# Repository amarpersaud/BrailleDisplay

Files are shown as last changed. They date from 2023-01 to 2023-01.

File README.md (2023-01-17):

# Electronic Braille Display Module
Electronic Refreshable Braille Display Module (8 dot) which uses latching solenoids with an integrated microcontroller and H-bridge drivers to drive each dot.

The design is inspired by MOLBED, a design which uses a latching solenoid formed by a solenoid coil, two metric nuts or washers, and neodymium magnets alongside 3d printed components. Some aspects of this design are similar, including the solenoid style of actuation. Several iterations of the design exist.  

## Physical Design Versions

### Version A (discontinued)
The first design consideration (Version A) (discontinued) consisted of an solenoid powered device with a physical latching mechanism, rather than the magnetic mechanism of MOLBED. Due to its low actuation force, complexity, and issues with actuation errors due to physical loading while actuating, it is no longer a consideration. Another major downside to this design is that all solenoids representing an extended dot must be simultaneously powered due to the physical latching mechanism locking all 8 dots at the same time, increasing the instantaneous power draw. Version B and C are two separate branching models under consideration.

### Version B
Version B uses a directly actuated latching solenoid which utilizes the force of a magnet hold the solenoid in the top position, more similar to MOLBED. The design is altered to reduce part count and complexity while improving actuation and holding force, and giving space to integrate electronics. This produces a module which has self contained drivers, with high holding force in the extended position, and high actuation force.

### Version C
Version C uses a similar solenoid as is used in Version B, however its mechanism is similar to that of multi-layer devices. The patent on such devices is no longer active and thus such devices can be produced. This uses a moving ramped section to push the dots up and down. The ramp allows a greater mechanical advantage, raising the actuation force. The holding force is also extremely high, as the pin is physically blocked from moving downwards. 

Due to the physical advantage in actuation for Version C, a lower force is needed to actuate the dots, meaning a larger or less efficient solenoid can be used. This means that the rare earth magnets (e.g. neodymium magnets) used in Version B could be swapped for weaker but more renewable and cheaper magnets.

The disadvantage of the Version C design is that it is much less compact. This is potentially an acceptable tradeoff, as it could be cheaper and more environmentally friendly, while allowing more room for electronics, but is harder to tile in a multi-row display. Due to the tradeoffs, it was deemed better to explore and refine both options in order to determine which design holds the advantage.

## Electronics
Electronics design for the device involved creation of a development board, codevelopment of the firmware and hardware using the development board, and a final board design created based on the physical CAD design. 

The development board design is available in the Hardware folder, and involves a microcontroller which drives two shift registers to control four dual H-bridge drivers, thus one H-bridge per dot or solenoid. The board is fairly large with hand solderable 0603 components, with additional GPIO and headers for development of the TWI/I2C, USART, and SPI communication protocols.

The development of the final board is still in progress and will likely consist of several boards connected together in order to keep it compact enough to fit inside the module (limited in size by the Braille standard) while still using off the shelf components.

## Firmware
The firmware for the device is still being developed. The firmware running on the embedded microcontroller creates several virtual registers which can be written to or read. Particularly, the device maintains a single byte register representing the 8 dots to be displayed, feedback sensing of the dot positions, operation completion, error detection using position detection as closed loop feedback, and configuration such as wether to immediately display the dots when the register is written or to automatically attempt to re-write to the display should an error in a dot be detected.

The device ID consists of two bytes written to EEPROM, allowing overwriting of the ID should the firmware be flashed to use many characters on a single bus such as with TWI or USART without an explicit select pin as afforded by SPI. This also allows setting the hardware address during runtime, without reflashing the firmware.

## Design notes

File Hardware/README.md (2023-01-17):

# Hardware
The hardware consists of a 3d CAD model for the module, an external development board for driving the latching solenoids, and several PCBs that form the final driver for the embedded device. 

## Definitions
- Holding force - Force the extended dots can withstand before device failure or depression of dot
- Actuation force - Force that an individual dot is capable of exerting while extending

## CAD model
Inspiration for the design came from the MOLBED project, and some aspects of the design are similar, including the solenoid style of actuation. Several iterations of the design exist. The first design consideration (Version A) (discontinued) consisted of an solenoid powered device with a physical latching mechanism, rather than the magnetic mechanism of MOLBED. Due to its low actuation force, complexity, and issues with actuation errors due to physical loading while actuating, it is no longer a consideration. Version B and C are two separate branching models under consideration. 

Version B uses a directly actuated latching solenoid which utilizes the force of a magnet hold the solenoid in the top position, more similar to MOLBED. The design is altered to reduce part count and complexity while improving actuation and holding force, and giving space to integrate electronics. This produces a module which has self contained drivers, with high holding force in the extended position, and high actuation force.

Version C uses a similar solenoid as is used in Version B, however its mechanism is similar to that of multi-layer devices. The patent on such devices is no longer active and thus such devices can be produced. This uses a moving ramped section to push the dots up and down. The ramp allows a greater mechanical advantage, raising the actuation force. The holding force is also extremely high, as the pin is physically blocked from moving downwards. 

Due to the physical advantage in actuation, a lower force is needed to actuate the dots, meaning a larger or less efficient solenoid can be used. This means that the rare earth magnets (e.g. neodymium magnets) used in Version B could be swapped for weaker but more renewable and cheaper magnets.

The disadvantage of the Version C design is that it is much less compact. This is potentially an acceptable tradeoff, as it could be cheaper and more environmentally friendly, while allowing more room for electronics, but is harder to tile in a multi-row display. Due to the tradeoffs, it was deemed better to explore and refine both options in order to determine which design holds the advantage.

## Development board - V0.1

The development board is available in the Development board folder.

<p align="center">
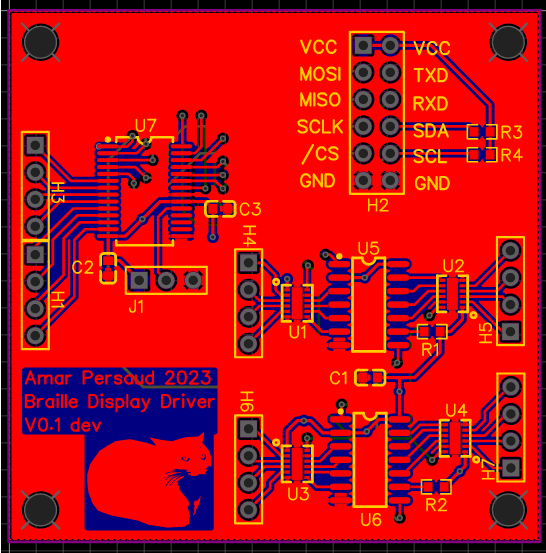
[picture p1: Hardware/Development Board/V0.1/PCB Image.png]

</p>

The board features an ATMEGA808-XUR microcontroller and two SN74HCS264DR shift registers to control four DRV8836DSSR ICs, each of which is capable of driving two bi-directional loads (headers H4-H7). Additionally, the header on the left (H1/H3) allows for 8x GPIO (for reading dot position for closed loop control), and the header on the top (H2) allows access to VCC(3.3V/5V), I2C/TWI, USART, and SPI communications. This allows for development of the software to communicate over SPI/USART/TWI with a higher level controller. Header J1 allows programming of the microcontroller via UPDI.

The board was developed in EasyEDA as it is a simple board whose sole purpose is to develop the firmware for the device; the board simply connects a microcontroller to shift registers, and shift registers to H-bridge drivers.

## Embedded PCB
The embedded device controller is currently in development. The device will be completed after finalization of the physical model.

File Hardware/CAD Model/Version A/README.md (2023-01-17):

# Version A
Version A consisted of an solenoid powered device with a physical latching mechanism, rather than the magnetic mechanism of MOLBED. 
Due to its low actuation force, complexity, and issues with actuation errors due to physical loading while actuating, it is no longer a consideration. 
Version A.1 and A.2 are two designs that are similar with slightly different operation. A.1 was the main design considered.

# Version A.1
Version A.1 is shown below: 
<p align="center">
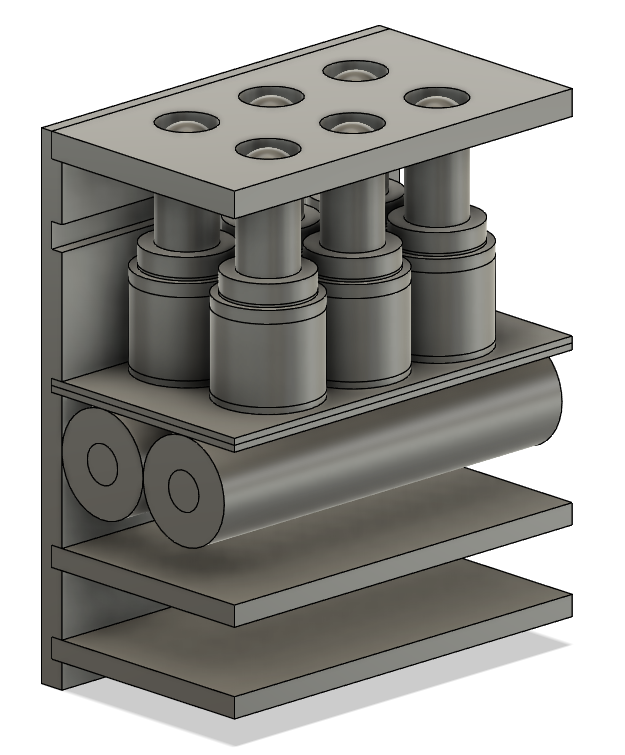
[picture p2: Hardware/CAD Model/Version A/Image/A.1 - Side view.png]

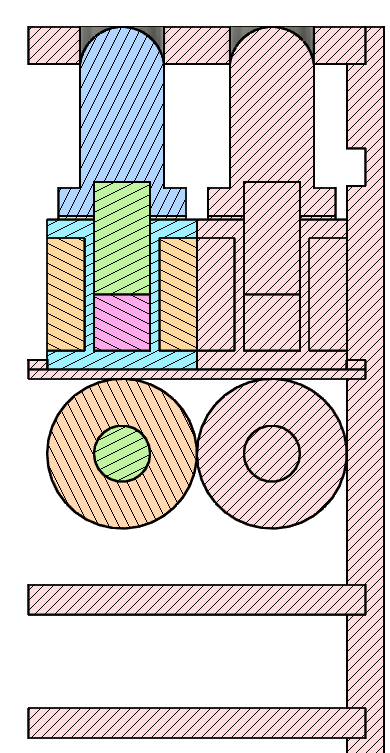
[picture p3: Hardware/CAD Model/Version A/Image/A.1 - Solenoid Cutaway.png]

</p>

The left wall is excluded for a better view of the internals, however it is identical to the right wall.

In the cutaway, the sections are labelled as follows:
- Blue - Plastic dot cap which the user physically interracts with
- Green - Iron or steel ferromagnetic rods
- Pink - Neodymium magnet
- Aqua - Plastic spool for holding the magnet wire which forms the solenoid
- Orange - Solenoid or electromagnet coil

The slot on the right wall allows for a sliding grid to be employed. When a dot is depressed, the bars of the grid go over the lip on the dot's cap. When a dot is extended, the bar passes below the lip and holds the dot up. This forms a physical latching mechanism. On the bottom, the horizontal electromagnet allows actuation of the grid via a lever linkage. Below the two electromagnets are two PCB layers with clearance for components. A ferromagnetic rod is used in the electromagnet to increase its strength, and in the solenoid to increase the permeability.

Issues with this design include low area on the circuit boards, a large space taken up by the electromagnets, high part count and complexity, susceptibility to wear and damage, a requirement for close tolerances, and the possibility for actuation failure.

# Version A.2
Version A.2 is shown below: 
<p align="center">
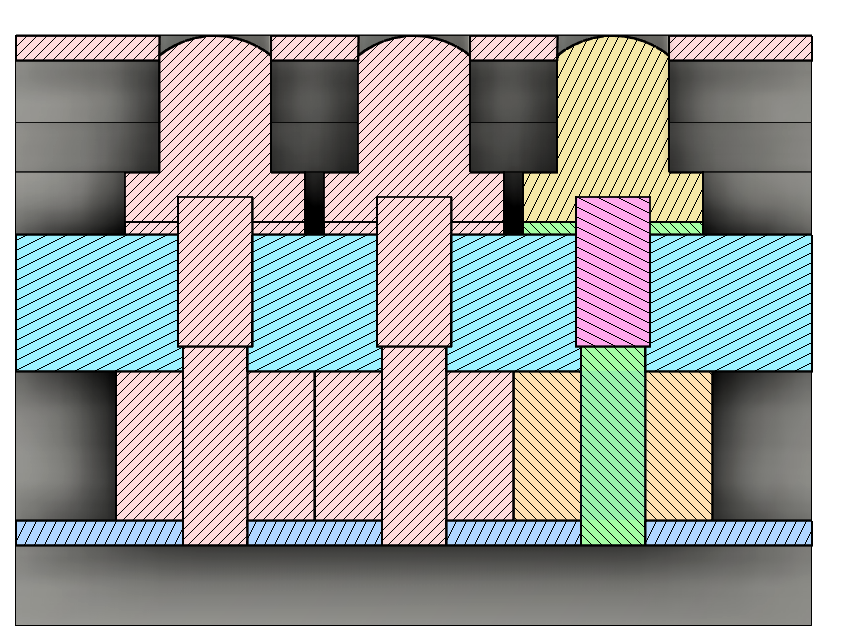
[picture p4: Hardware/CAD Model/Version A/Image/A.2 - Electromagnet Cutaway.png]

</p>

Version A.2 is design which takes a slightly different approach and was abandoned as well.

In the cutaway, the sections are labelled as follows:
- Yellow - Plastic dot cap which the user physically interracts with
- Horizontal Green Washer - Felt or soft material lower actuation noise
- Vertical Green Rod - Iron or steel ferromagnetic rods
- Pink - Neodymium magnet
- Aqua - Plastic for casing
- Blue - Plastic or PCB 
- Orange - Solenoid or electromagnet coil

This design has many drawbacks, including having a high retraction force but a much smaller actuation force, and relying on the physical actuation gives higher complexity.

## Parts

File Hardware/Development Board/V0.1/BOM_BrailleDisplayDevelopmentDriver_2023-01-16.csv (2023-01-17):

ID | Name | Designator | Footprint | Quantity | Manufacturer Part | Manufacturer | Supplier | Supplier Part | Price
1 | 0.1u | C1,C2,C3 | C0603 | 3
2 | HDR-F-2.54_1x4 | H1,H3,H4,H5,H6,H7 | HDR-F-2.54_1X4 | 6 |  |  | LCSC | C225501 | 0.013
3 | HDR-F-2.54_2x6 | H2 | HDR-F-2.54_2X6 | 1 |  |  | LCSC | C36191 | 0.011
4 | HDR-M-2.54_1x3 | J1 | HDR-M-2.54_1X3 | 1 |  |  | LCSC | C180248 | 0.031
5 | 1k | R1,R2 | R0603 | 2
6 | 4.7k | R3,R4 | R0603 | 2
7 | DRV8836DSSR | U1,U2,U3,U4 | WSON-12_L2.0-W3.0-P0.50-BL-EP | 4 | DRV8836DSSR | TI(德州仪器) | LCSC | C191002 | 0.249
8 | SN74HCS264DR | U5,U6 | SOIC-14_L8.6-W3.9-P1.27-LS6.0-BL | 2 | SN74HCS264DR | TI(德州仪器) | LCSC | C2861157 | 0.019
9 | ATMEGA808-XUR | U7 | SSOP-28_L10.2-W5.3-P0.65-LS7.8-BL | 1 | ATMEGA808-XUR | MICROCHIP(美国微芯) | LCSC | C2055567 | 0.336

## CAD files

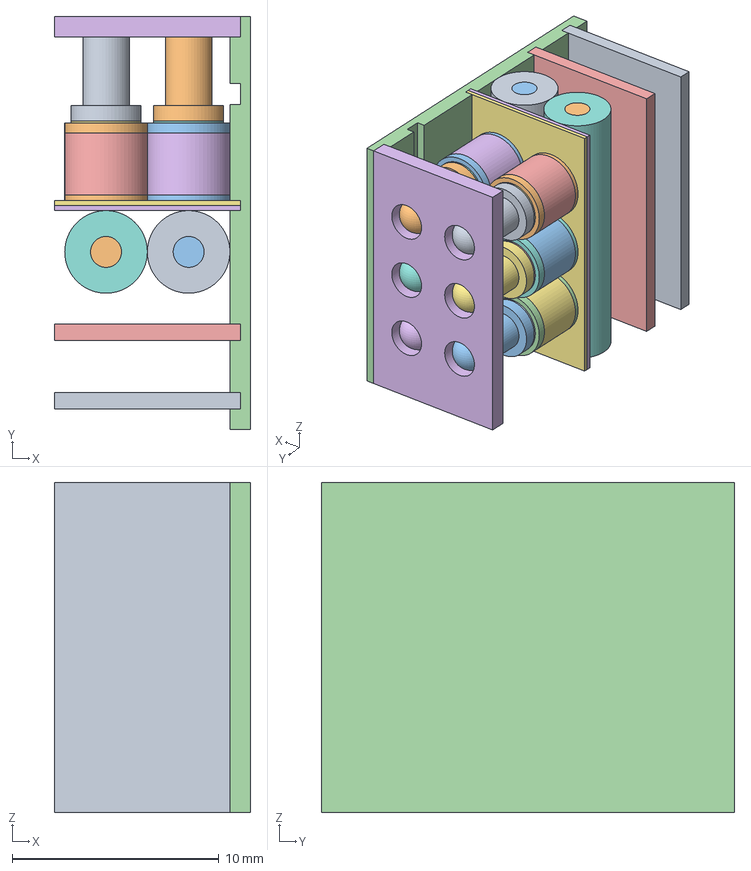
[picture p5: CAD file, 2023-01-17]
Hardware/CAD Model/Version A/CAD Files/Braille Display Module CAD VA.1.3mf
9.50 x 20.0 x 16.0 mm
Bottom PCB
Coil (1)
Coil (2)
Coil (3)
Coil (4)
Coil (5)
Coil
EnableCoil1
EnableCoil2
EnableCore1
EnableCore2
Felt (1)
Felt (2)
Felt (3)
Felt (4)
Felt (5)
Felt
Magnet (1)
Magnet (2)
Magnet (3)
Magnet (4)
Magnet (5)
Magnet Core (1)
Magnet Core (2)
Magnet Core (3)
Magnet Core (4)
Magnet Core (5)
Magnet Core
Magnet
Metal Plate
Middle Plate
Pin (1)
Pin (2)
Pin (3)
Pin (4)
Pin (5)
Pin
PinHat (1)
PinHat (2)
PinHat (3)
PinHat (4)
PinHat (5)
PinHat
Right Side
Top PCB
Top Plate

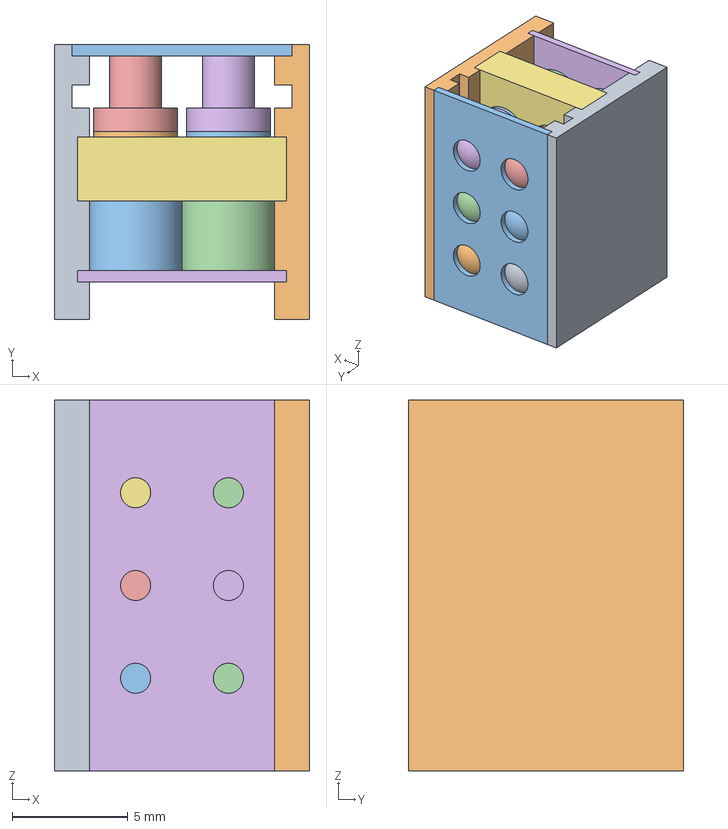
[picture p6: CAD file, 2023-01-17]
Hardware/CAD Model/Version A/CAD Files/Braille Display Module CAD VA.2.3mf
11.0 x 11.9 x 16.0 mm
Coil (1)
Coil (2)
Coil (3)
Coil (4)
Coil (5)
Coil
Core Bottom Plate
Core Top Plate
Felt
Left Plate
Right Plate
Top Plate

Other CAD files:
Hardware/CAD Model/Version A/CAD Files/Braille Display Module CAD VA.1.f3d
Hardware/CAD Model/Version A/CAD Files/Braille Display Module CAD VA.2.f3d

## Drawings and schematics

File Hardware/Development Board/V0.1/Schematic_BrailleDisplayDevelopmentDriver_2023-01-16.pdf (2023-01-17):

## Microcontroller

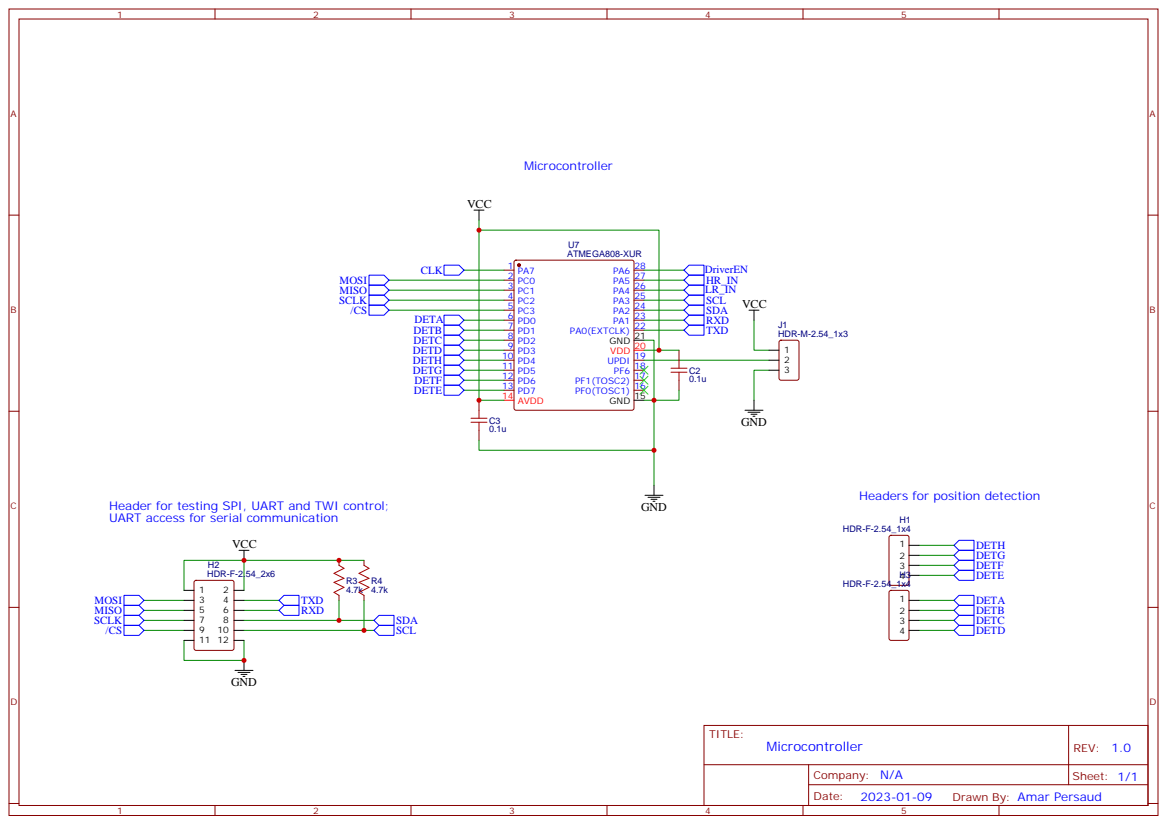
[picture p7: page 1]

Headers for position detection

Header for testing SPI, UART and TWI control;
UART access for serial communication

Drawn By: Amar Persaud

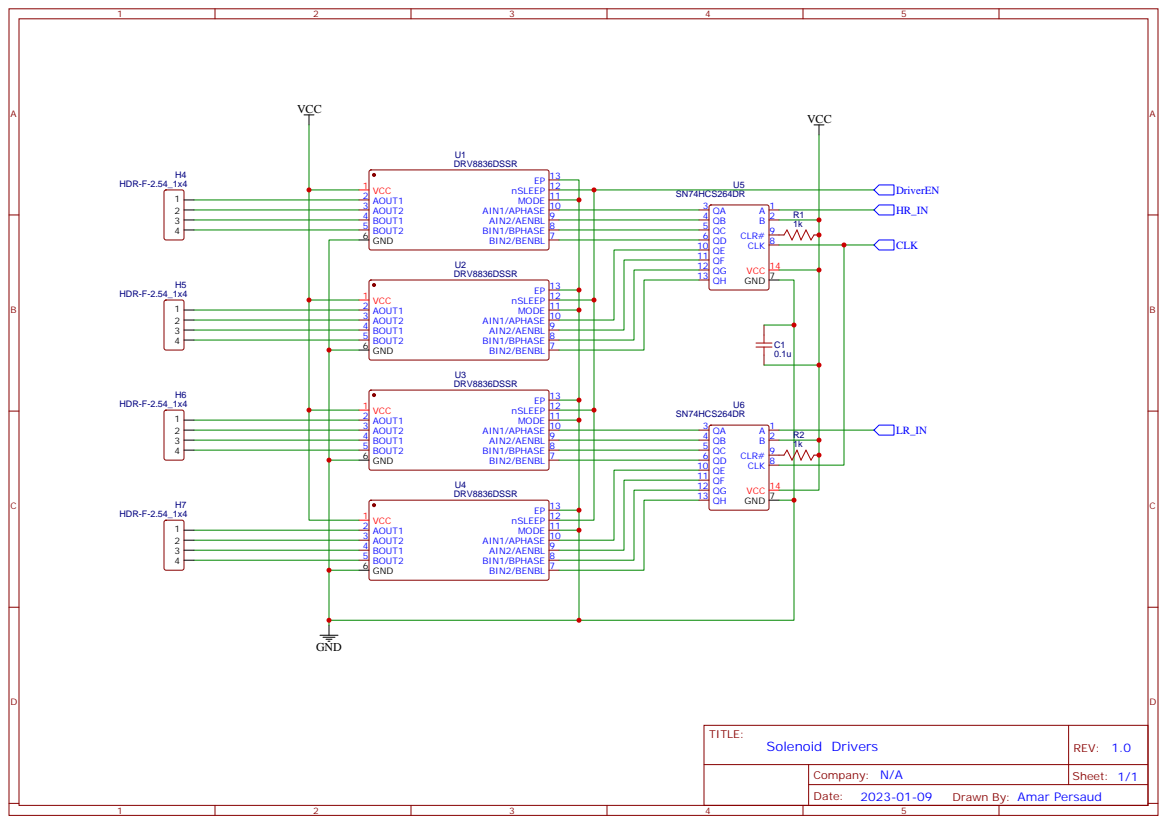
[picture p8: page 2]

Drawn By: Amar Persaud

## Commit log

2023-01-17 Add development board files
    [BOM_BrailleDisplayDevelopmentDriver_2023-01-16.csv]
2023-01-17 Fix PCB image
2023-01-17 Update readme with development PCB
2023-01-17 Add CAD files for VA.1 and VA.2
    [Braille Display Module CAD VA.1.3mf, Braille Display Module CAD VA.1.f3d, Braille Display Module CAD VA.2.3mf, Braille Display Module CAD VA.2.f3d]
